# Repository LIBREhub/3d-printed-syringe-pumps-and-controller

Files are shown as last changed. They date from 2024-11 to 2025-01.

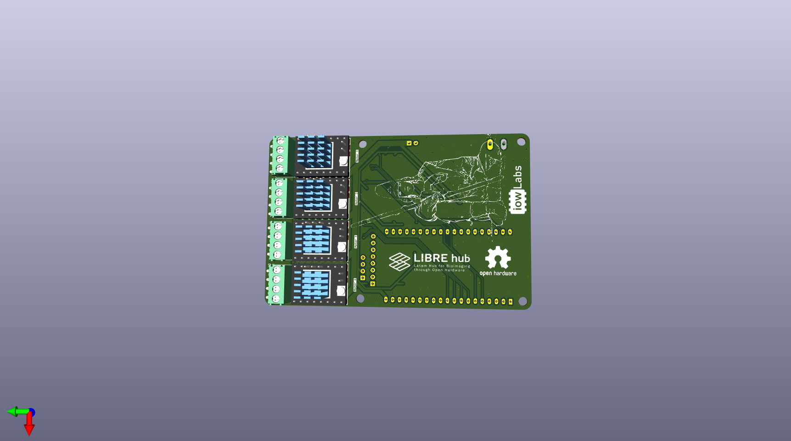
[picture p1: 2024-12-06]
electronics/syringe_pump_controller_module/_versions/ver1/syringe_pump_bottom.png

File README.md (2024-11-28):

# 3D printable syringe pumps and controller  

This project is a free and open-source design of versatile lab equipment - syringe pumps and a dual controller, here detailed for microfluidic droplet generation - a modification from this [Open-Source Syringe Pump design](https://doi.org/10.1134/S1061934820030156).

Find about more about this platform and other open-source hardware for bioimaging on the [LIBRE hub website](https://librehub.github.io/). Follow us! [#twitter](https://twitter.com/WenzelLab) [#YouTube](https://www.youtube.com/@librehub) [#LinkedIn](https://www.linkedin.com/company/92802424) [#instagram](https://www.instagram.com/wenzellab/) [#Printables](https://www.printables.com/@WenzelLab), [IIBM website](https://ingenieriabiologicaymedica.uc.cl/en/people/faculty/821-tobias-wenzel)

## Background

A syringe pump is a device that delivers precise and accurate amounts of fluid over a broad range of flow rates. These devices are versatile and can be used across various fields like healthcare, research, and development, playing a crucial role in scenarios such as controlled drug delivery in hospitals, chemical reaction control in labs, and more.

There are many 3D-printable syringe pump designs available, each with its unique features and capabilities. However, this [Open-Source Syringe Pump design](https://doi.org/10.1134/S1061934820030156) developed by the [Mass Spectrometry Research Group](https://www.mass-spec.ru/projects/diy/syringe_pump/eng/), Analytical Chemistry Division, Chemistry Department of Moscow State University, appealed to our LIBRE Hub team with its design and functionality.

Our goal with this modification and enhancement is to make this open-source syringe pump design more useful to microfluidics and generally more accessible, adaptable, and user-friendly, thus extending its potential use within the broader community.

## Usage

### Instructions
This Repository provides documentation on how to build the pumps and the controller. Just [follow the instructions here](https://wenzel-lab.github.io/syringe-pumps-and-controller/)

This project is documented with GitBuilding - an Open Source project for documenting hardware projects. For more information on the GitBuilding project or how
to install GitBuilding, please see the [GitBuilding website](http://gitbuilding.io)

## Design files and source code

* Hardware design
    * [Link to OnShape CAD files of printable syringe pump parts](https://cad.onshape.com/documents/20c077b452e92115525d4fed/w/71118f46b0924c1bb22b1150/e/9d30ca00efa721d242d78d3f?renderMode=0&uiState=64bd5f2a8bef574246b008b9)
    * [Link to OnShape CAD files of the printable controller enclosure](https://cad.onshape.com/documents/24a5022fafc4edd0c24874dd/w/35c6569cda7c2fa4439727d4/e/9dbcdcaba091e21e6a91c62c?renderMode=0&uiState=64bd5f3f0aa451311c1bb6ad)
* Software source code
    * [Code to upload onto the Raspberry Pi Pico controller](https://github.com/wenzel-lab/syringe-pumps-and-controller/blob/docu-v1/software/firmwareV1.ino)

### How do I edit the documentation?

To edit the documentation, you do not need to install anything, but you will need to
install something to build the final version of the documentation (such as a website).
The documentation files can be opened in a plain text editor such as Windows Notepad,
Notepad++, gedit, VS Code, etc. GitBuilding also comes with a browser-based editor that
displays a live display of the final HTML documentation.

If you have ever used [markdown](https://www.markdownguide.org/basic-syntax/), you will
notice that the files you are editing are markdown files. GitBuilding uses an extended
markdown syntax (that we call BuildUp). This allows you to keep track of parts in the
documentation. More detail on the documentation is available on the
[GitBuilding website](https://gitbuilding.io/syntax/). There is also additional
[syntax for configuration](https://gitbuilding.io/syntax/buildconfsyntax) and for
[part libraries](https://gitbuilding.io/syntax/builduplibrary/).

## Contribute

Enjoy building and using your improved Open-Source Syringe Pump! We look forward to hearing about your experiences and any further improvements you might have. Make a pull request or [open an issue](https://github.com/wenzel-lab/syringe-pumps-and-controller/issues/new).
For interactions in our team and with the community, apply the [GOSH Code of Conduct](https://openhardware.science/gosh-2017/gosh-code-of-conduct/).

## License

[GNU General Public License v3.0](LICENSE) by Tomás Astudillo, Matías Hurtado, Pierre Padilla-Huamantinco, Tobias Wenzel, and the [original design team](https://www.mass-spec.ru/projects/diy/syringe_pump/eng/). This project is Open Source Hardware - please acknowledge us when using the hardware or sharing modifications.

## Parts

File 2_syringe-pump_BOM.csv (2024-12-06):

Name in documentation | Category | Qty | Full Name | Notes
Back support - A | printedparts | 1
Back support - B | printedparts | 1
Carriage | printedparts | 1
Front support | printedparts | 1
Hand knob | printedparts | 2
Heat insert | mech | 6 | Heat inserts
Lead screw | mech | 1 | Threaded Rod
Lead screw nut | mech | 1 | Lead Screw Nut
Linear bearing | mech | 2 | Linear Bearing
Linear motion rods | mech | 2 | Linear Motion Rods
M2.5 hex key | tool | 1
M3 10mm screw | mech | 2 | Screw
M3 12mm screw | mech | 2 | Screw
M3 16mm screw | mech | 8 | Screw
M3 20mm screw | mech | 2 | Screw
M3 8mm screw | mech | 4 | Screw
M3 hex key | tool | 1
M3 nut | mech | 9
M4 10mm screw | mech | 4 | Screw
M4 hex key | tool | 1
Motor coupling | mech | 1 | Motor Coupling
NEMA 17 motor | elect | 1 | Stepper Motor Nema 17
Planetary gearbox 100:1 | mech | 1 | Planetary Gearbox
Soldering iron | tool | 1
Syringe holder | printedparts | 1

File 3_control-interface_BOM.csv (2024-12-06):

Name in documentation | Category | Qty | Full Name | Notes
10 cm female-female jumper | elect | 7
10 cm male-female jumper | elect | 8
20 cm female-female jumper | elect | 12
40 pin header | elect | 1
5.5mm female jack connector | elect | 1
Back cover | printedparts | 1
Electronics holder | printedparts | 1
Interface base | printedparts | 1
Interface panel | printedparts | 1
LCD adapter | printedparts | 1
LCD screen | elect | 1 | LCD Screen
M3 10mm screw | mech | 8 | Screw
M3 16mm screw | mech | 4 | Screw
M3 25mm screw | mech | 1 | Screw
M3 nut | mech | 14
Membrane 4x4 keypad | elect | 1
Raspberry Pi Pico | elect | 1
TMC2209 driver | elect | 2 | Silent Driver + Heatsink
Voltage regulator | elect | 1

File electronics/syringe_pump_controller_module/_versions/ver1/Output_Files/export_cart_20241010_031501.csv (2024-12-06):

LCSC Part Number | Manufacture Part Number | Manufacturer | Package | Customer # | Description | RoHS | Order Qty. | Min\Mult Order Qty. | Unit Price($) | Ext.Price($) | Product Link
C14663 | CC0603KRX7R9BB104 | YAGEO | 0603 |  | 50V 100nF X7R ±10% 0603 Multilayer Ceramic Capacitors MLCC - SMD/SMT ROHS | yes | 100 | 100 | 0.0020 | 0.20 | https://www.lcsc.com/product-detail/multilayer-ceramic-capacitors-mlcc-smd-smt_yageo-cc0603krx7r9bb104_C14663.html
C28323 | CL21B105KBFNNNE | Samsung Electro-Mechanics | 0805 |  | 50V 1uF X7R ±10% 0805 Multilayer Ceramic Capacitors MLCC - SMD/SMT ROHS | yes | 50 | 50 | 0.0088 | 0.44 | https://www.lcsc.com/product-detail/multilayer-ceramic-capacitors-mlcc-smd-smt_samsung-electro-mechanics-cl21b105kbfnnne_C28323.html
C5162345 | CS1E221M-CRF10 | ROQANG | SMD,D8xL10.5mm |  | 220uF 25V 183mA@120Hz ±20% SMD,D8xL10.5mm Aluminum Electrolytic Capacitors - SMD ROHS | yes | 10 | 10 | 0.0604 | 0.60 | https://www.lcsc.com/product-detail/aluminum-electrolytic-capacitors-smd_roqang-cs1e221m-crf10_C5162345.html
C5162349 | CS1E331M-CRF10 | ROQANG | SMD,D8xL10.5mm |  | 330uF 25V 228mA@120Hz ±20% SMD,D8xL10.5mm Aluminum Electrolytic Capacitors - SMD ROHS | yes | 10 | 10 | 0.0444 | 0.44 | https://www.lcsc.com/product-detail/aluminum-electrolytic-capacitors-smd_roqang-cs1e331m-crf10_C5162349.html
C3019736 | ACDBB540-HF | Comchip | SMB |  | 40V Independent Type 550mV@5A 5A SMB Schottky Diodes ROHS | yes | 5 | 5 | 0.2341 | 1.17 | https://www.lcsc.com/product-detail/schottky-diodes_comchip-acdbb540-hf_C3019736.html
C12624 | KT-0603G | Hubei KENTO Elec | 0603 |  | Emerald 0603 LED Indication - Discrete ROHS | yes | 50 | 50 | 0.0104 | 0.52 | https://www.lcsc.com/product-detail/led-indication-discrete_hubei-kento-elec-kt-0603g_C12624.html
C553921 | S1206-F-1.0A | SART(Nanjing Sart Tech) | 1206 |  | 50A SMD Fuse 1A 32V 1206 Disposable fuses ROHS | yes | 10 | 10 | 0.0686 | 0.69 | https://www.lcsc.com/product-detail/disposable-fuses_sart-nanjing-sart-tech-s1206-f-1-0a_C553921.html
C2840319 | TY500-5.0-02P-14-00AH | Toponelec | Plugin,P=5mm |  | 1x2P 20A -40℃~+105℃ 300V Green 12~30 Direct Insert 5mm 1~2.5 1 2 Plugin,P=5mm Screw Terminal Blocks ROHS | yes | 5 | 1 | 0.1999 | 1.00 | https://www.lcsc.com/product-detail/screw-terminal-blocks_toponelec-ty500-5-0-02p-14-00ah_C2840319.html
C557656 | XY350V-3.5-4P | Ningbo Xinlaiya Elec. | Plugin,P=3.5mm |  | Copper 1x4P Tin 3.5mm 1 1 4 7A 300V Green 18~24 Direct Insert Plugin,P=3.5mm Screw Terminal Blocks ROHS | yes | 20 | 5 | 0.2307 | 4.61 | https://www.lcsc.com/product-detail/screw-terminal-blocks_ningbo-xinlaiya-elec-xy350v-3-5-4p_C557656.html
C8677 | XH-2Y | BOOMELE(Boom Precision Elec) | P=2.5mm |  | 2.5mm 1x2P XH 2 1 P=2.5mm Housings (Wire To Board / Wire To Wire ) ROHS | yes | 100 | 100 | 0.0035 | 0.35 | https://www.lcsc.com/product-detail/housings-wire-to-board-wire-to-wire_boomele-boom-precision-elec-xh-2y_C8677.html
C20079 | XH-2A | BOOMELE(Boom Precision Elec) | Plugin,P=2.5mm |  | 1x2P 2P XH 1 2.5mm 2 Plugin,P=2.5mm Wire To Board Connector ROHS | yes | 100 | 100 | 0.0067 | 0.67 | https://www.lcsc.com/product-detail/wire-to-board-connector_boomele-boom-precision-elec-xh-2a_C20079.html
C5116530 | PM2.54-1*4 | ZHOURI | Plugin,P=2.54mm |  | 2.54mm 2.54mm Single Row 2.5A 4P -40℃~+105℃ Direct Insert 1x4P Top 8.5mm Square Hole Plugin,P=2.54mm Female Headers ROHS | yes | 5 | 5 | 0.0711 | 0.36 | https://www.lcsc.com/product-detail/female-headers_zhouri-pm2-54-1-4_C5116530.html
C5224027 | PM2.54-1*8 | ZHOURI | Plugin,P=2.54mm |  | 2.54mm 2.54mm Single Row 2.5A 8P -40℃~+105℃ Direct Insert 1x8P Top 8.5mm Square Hole Plugin,P=2.54mm Female Headers ROHS | yes | 5 | 5 | 0.0916 | 0.46 | https://www.lcsc.com/product-detail/female-headers_zhouri-pm2-54-1-8_C5224027.html
C2929502 | CYH127-33UH | SHOU HAN | SMD,12.3x12.3mm |  | 3A 33uH ±20% 64.8mΩ SMD,12.3x12.3mm Inductors (SMD) ROHS | yes | 5 | 5 | 0.2669 | 1.33 | https://www.lcsc.com/product-detail/inductors-smd_shou-han-cyh127-33uh_C2929502.html
C98220 | RC0603FR-0710KL | YAGEO | 0603 |  | 100mW Thick Film Resistors 75V ±100ppm/℃ ±1% 10kΩ 0603 Chip Resistor - Surface Mount ROHS | yes | 200 | 100 | 0.0010 | 0.20 | https://www.lcsc.com/product-detail/chip-resistor-surface-mount_yageo-rc0603fr-0710kl_C98220.html
C22548 | RC0603FR-071KL | YAGEO | 0603 |  | 100mW Thick Film Resistors 75V ±100ppm/℃ ±1% 1kΩ 0603 Chip Resistor - Surface Mount ROHS | yes | 100 | 100 | 0.0010 | 0.10 | https://www.lcsc.com/product-detail/chip-resistor-surface-mount_yageo-rc0603fr-071kl_C22548.html
C25995 | 0603WAJ0332T5E | UNI-ROYAL(Uniroyal Elec) | 0603 |  | 100mW Thick Film Resistors 75V ±100ppm/℃ ±5% 3.3kΩ 0603 Chip Resistor - Surface Mount ROHS | yes | 100 | 100 | 0.0009 | 0.09 | https://www.lcsc.com/product-detail/chip-resistor-surface-mount_uni-royal-uniroyal-elec-0603waj0332t5e_C25995.html
C51118 | AP2112K-3.3TRG1 | Diodes Incorporated | SOT-25-5 |  | 65dB@(100Hz,1kHz) 600mA Fixed 3.3V Positive electrode 6V SOT-25-5 Voltage Regulators - Linear, Low Drop Out (LDO) Regulators ROHS | yes | 5 | 5 | 0.0692 | 0.35 | https://www.lcsc.com/product-detail/voltage-regulators-linear-low-drop-out-ldo-regulators_diodes-incorporated-ap2112k-3-3trg1_C51118.html
C51661 | XL4015E1 | XLSEMI | TO-263-5 |  | Step-down type 5A 8V~36V TO-263-5 DC-DC Converters ROHS | yes | 5 | 1 | 0.5826 | 2.91 | https://www.lcsc.com/product-detail/dc-dc-converters_xlsemi-xl4015e1_C51661.html
C22396383 | PCF8574DWR(UMW) | UMW(Youtai Semiconductor Co., Ltd.) | SOIC-16-300mil |  | SOIC-16-300mil I/O Expanders ROHS | yes | 5 | 1 | 0.4569 | 2.28 | https://www.lcsc.com/product-detail/i-o-expanders_umw-youtai-semiconductor-co-ltd-pcf8574dwr-umw_C22396383.html
C128392 | PCA9555PW,118 | NXP Semicon | TSSOP-24 |  | 16 400kHz TSSOP-24 I/O Expanders ROHS | yes | 5 | 1 | 0.8596 | 4.30 | https://www.lcsc.com/product-detail/i-o-expanders_nxp-semicon-pca9555pw-118_C128392.html
C529577 | ESP32-WROOM-32D-N8 | Espressif Systems | SMD,18x25.5mm |  | SMD,18x25.5mm WiFi Modules ROHS | yes | 5 | 1 | 4.0019 | 20.01 | https://www.lcsc.com/product-detail/wifi-modules_espressif-systems-esp32-wroom-32d-n8_C529577.html

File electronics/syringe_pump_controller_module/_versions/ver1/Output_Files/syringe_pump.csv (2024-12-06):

Reference | Value | Datasheet | Footprint | Qty | DNP
C1,C3,C4,C5,C6,C19,C20,C21,C22 | 1u |  | Capacitor_SMD:C_0805_2012Metric | 9
C2 | 220uF | ~ | Capacitor_SMD:CP_Elec_8x10.5 | 1
C7 | 330uF | ~ | Capacitor_SMD:CP_Elec_8x10.5 | 1
C13,C14,C15,C16,C17,C18 | 100n |  | Capacitor_SMD:C_0603_1608Metric | 6
D1,D3,D4 | LED | ~ | LED_SMD:LED_0603_1608Metric | 3
D2 | B540 | ~ | Diode_SMD:D_SMB_Handsoldering | 1
F2 | FUSE |  | Fuse:Fuse_1206_3216Metric | 1
J1 | IN |  | IoWLabsConnectors:Tb-2x1-5p-TH-V | 1
J2 | ON OFF |  | Connector_PinHeader_2.54mm:PinHeader_1x02_P2.54mm_Vertical | 1
J4,J5,J8,J9 | HDR-4x1 |  | TerminalBlock_Phoenix:TerminalBlock_Phoenix_PT-1,5-4-3.5-H_1x04_P3.50mm_Horizontal | 4
J6,J7,J10,J11 | EndSwitch |  | IoWLabsConnectors:JST-XH-2x1-2.5p-TH-V | 4
J12 | Conn_01x04 | ~ | Connector_PinSocket_2.54mm:PinSocket_1x04_P2.54mm_Vertical | 1
J13 | Conn_01x08 | ~ | Connector_PinSocket_2.54mm:PinSocket_1x08_P2.54mm_Vertical | 1
L1 | 47uH | ~ | Inductor_SMD:L_12x12mm_H8mm | 1
R1,R2,R3,R19,R20,R23,R24 | 1k |  | Resistor_SMD:R_0603_1608Metric | 7
R4,R13,R14,R15,R16,R17,R18 | 10K |  | Resistor_SMD:R_0603_1608Metric | 7
R5 | 3.3K |  | Resistor_SMD:R_0603_1608Metric | 1
R7,R8,R21,R22,R25,R26,R27,R28,R29,R30,R31 | 10k |  | Resistor_SMD:R_0603_1608Metric | 11
U1 | AP2112K-3.3 | https://www.diodes.com/assets/Datasheets/AP2112.pdf | Package_TO_SOT_SMD:SOT-23-5 | 1
U2 | XL4015 | http://www.xlsemi.net/datasheet/XL4015%20datasheet-English.pdf | Package_TO_SOT_SMD:TO-263-5_TabPin3 | 1
U5 | MCP23017_SO | http://ww1.microchip.com/downloads/en/DeviceDoc/20001952C.pdf | Package_SO:SOIC-28W_7.5x17.9mm_P1.27mm | 1
U6 | PCF8574 | http://www.nxp.com/docs/en/data-sheet/PCF8574_PCF8574A.pdf | Package_SO:SOIC-16W_7.5x10.3mm_P1.27mm | 1
U7 | ESP32-DevKitC | https://docs.espressif.com/projects/esp-idf/zh_CN/latest/esp32/hw-reference/esp32/get-started-devkitc.html | Espressif:ESP32-DevKitC | 1
X1,X2,X3,X4 | ~ |  | IoWLabsModules:TCM2209 | 4

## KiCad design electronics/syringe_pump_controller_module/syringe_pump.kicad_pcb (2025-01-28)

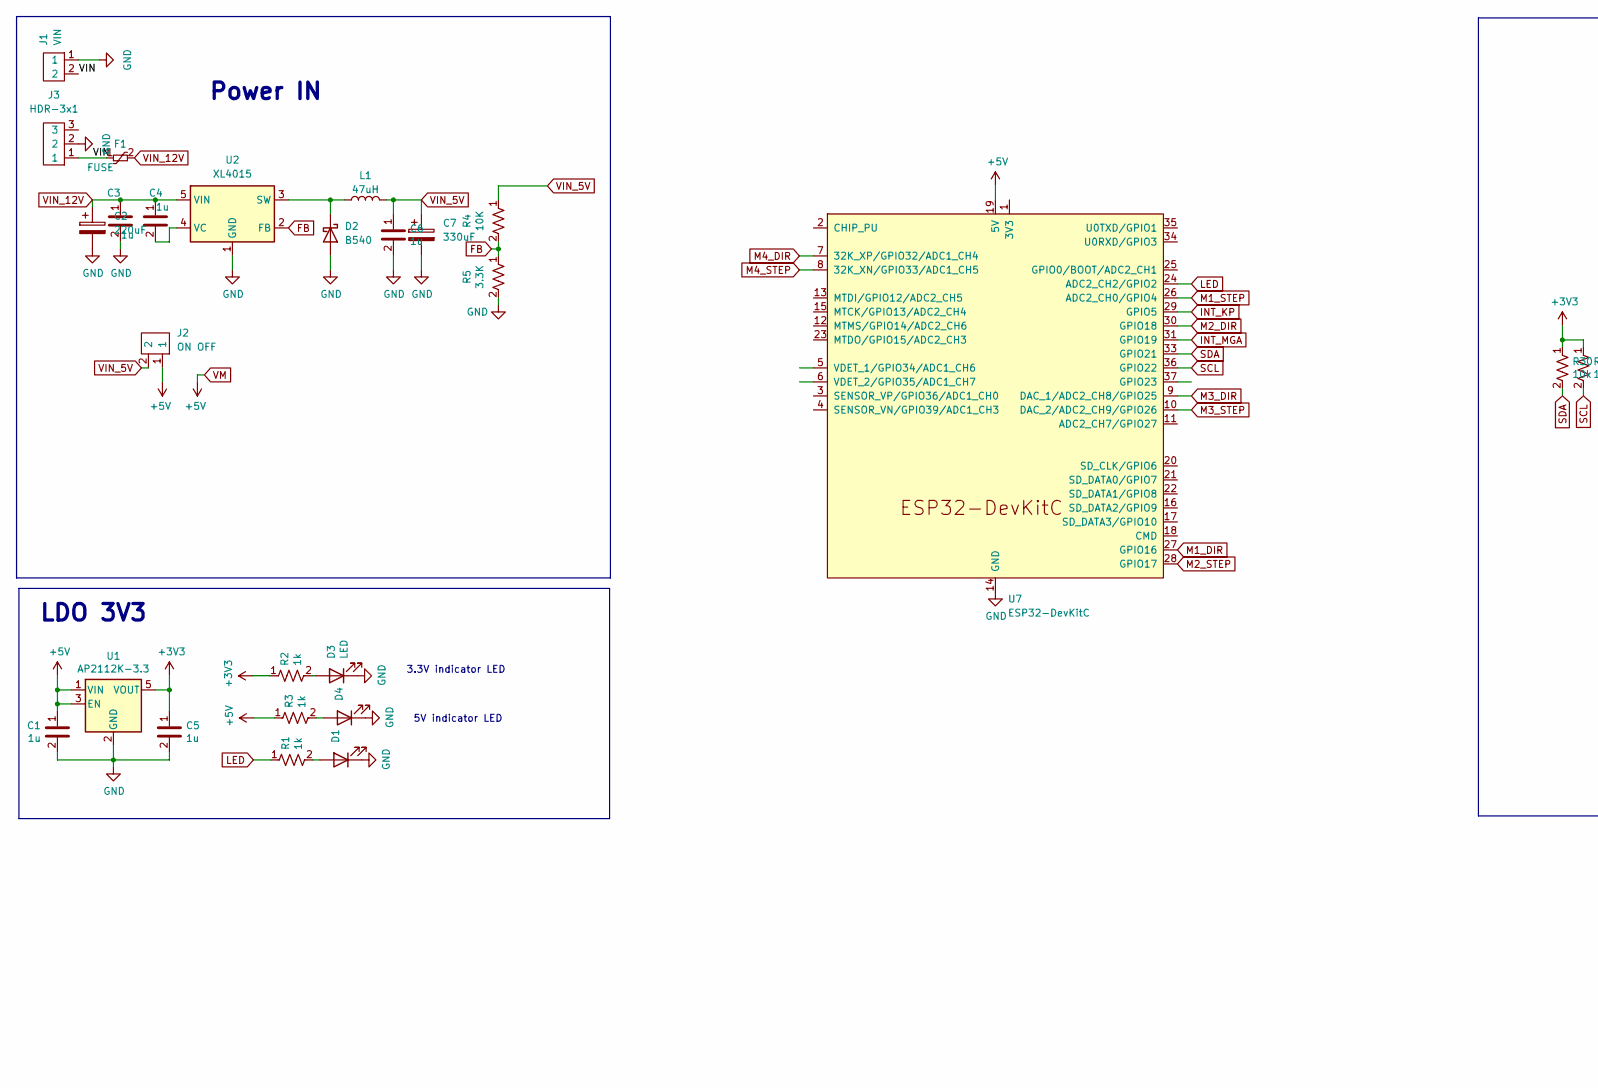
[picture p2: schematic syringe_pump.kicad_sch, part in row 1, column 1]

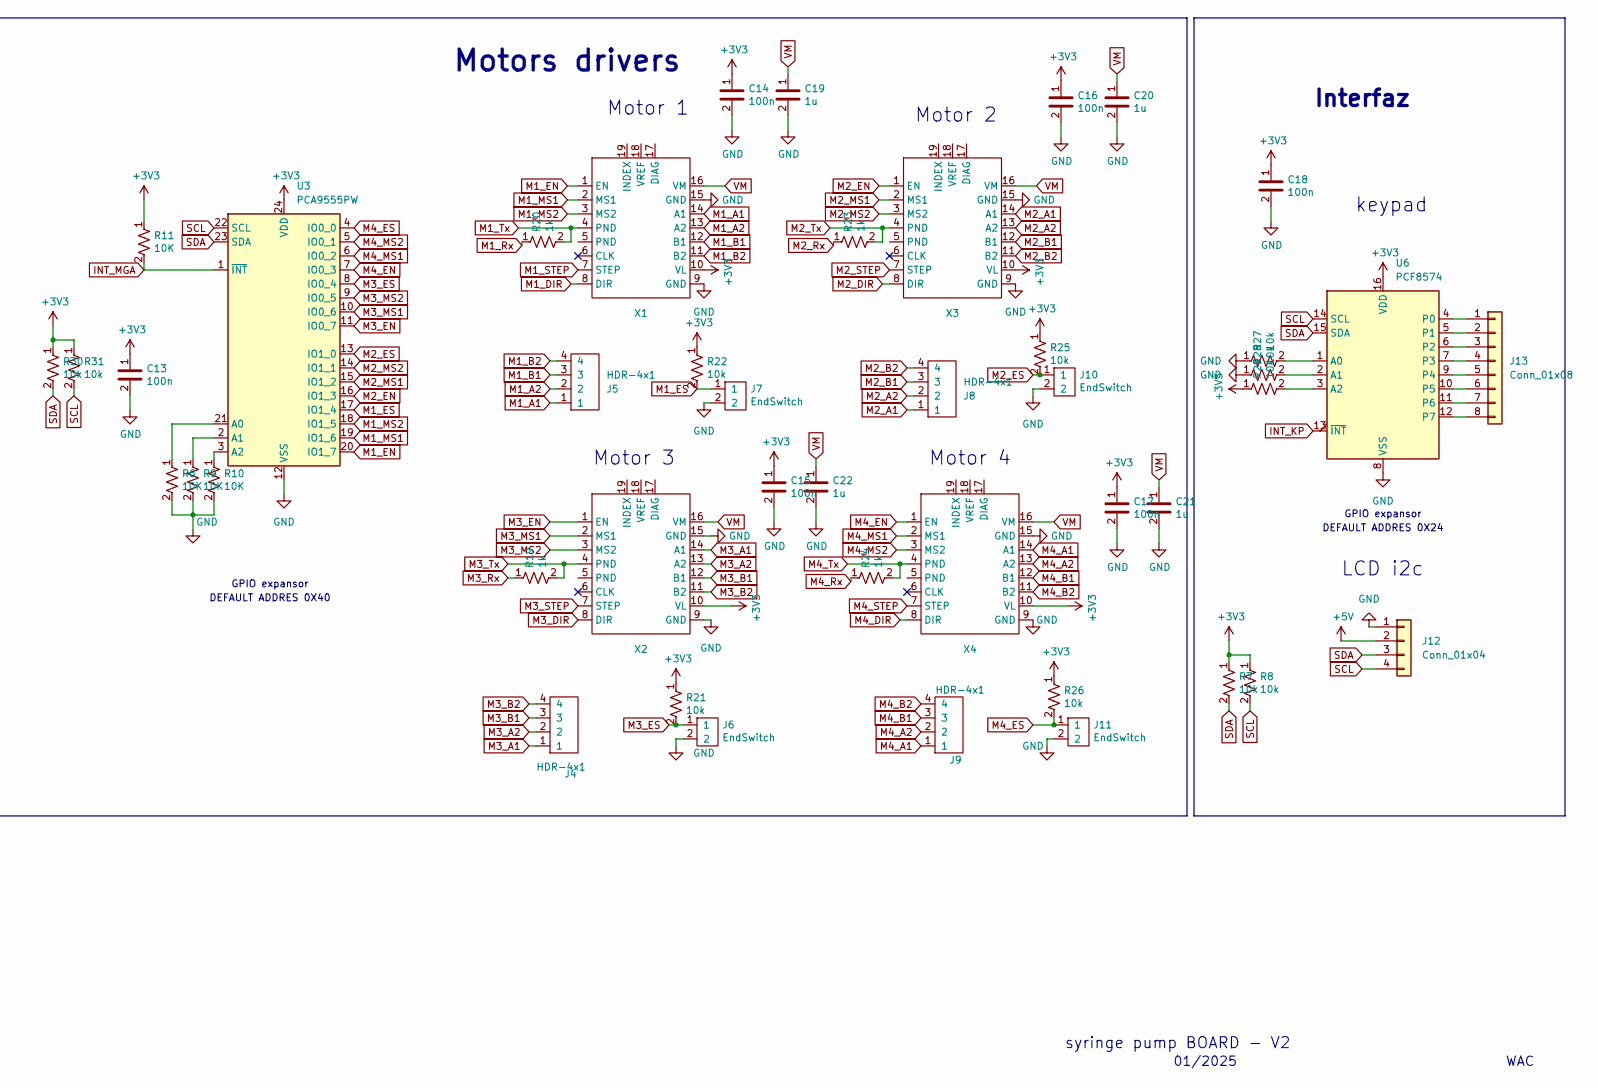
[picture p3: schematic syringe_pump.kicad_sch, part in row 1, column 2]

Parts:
C1, C3, C4, C5, C6, C19, C20, C21, C22: 1u; C_0805_2012Metric; Voltage rated 16V
C2: 220uF; CP_Elec_8x10.5; Voltage 50V
C7: 330uF; CP_Elec_8x10.5; Voltage 25V
C13, C14, C15, C16, C17, C18: 100n; C_0603_1608Metric; Voltage rated 16V
D1, D3, D4: LED; LED_0603_1608Metric
D2: B540; D_SMB_Handsoldering
F1: FUSE; Fuse_1206_3216Metric
J1: VIN; Tb-2x1-5p-TH-V
J2: ON OFF; PinHeader_1x02_P2.54mm_Vertical
J3: HDR-3x1; BarrelJack_Horizontal
J4, J5, J8, J9: HDR-4x1; TerminalBlock_Phoenix_PT-1,5-4-3.5-H_1x04_P3.50mm_Horizontal
J6, J7, J10, J11: EndSwitch; JST-XH-2x1-2.5p-TH-V
J12: Conn_01x04; PinSocket_1x04_P2.54mm_Vertical
J13: Conn_01x08; PinSocket_1x08_P2.54mm_Vertical
L1: 47uH; L_12x12mm_H8mm
R1, R2, R3, R19, R20, R23, R24: 1k; R_0603_1608Metric
R4, R6, R9, R10, R11: 10K; R_0603_1608Metric
R5: 3.3K; R_0603_1608Metric
R7, R8, R21, R22, R25, R26, R27, R28, R29, R30, R31: 10k; R_0603_1608Metric
U1: AP2112K-3.3; SOT-23-5
U2: XL4015; TO-263-5_TabPin3
U3: PCA9555PW; TSSOP-24_4.4x7.8mm_P0.65mm
U6: PCF8574; SOIC-16W_7.5x10.3mm_P1.27mm
U7: ESP32-DevKitC
X1, X2, X3, X4: TCM2209

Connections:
+3V3: C5.1, C13.1, C14.1, C15.1, C16.1, C17.1, C18.1, R2.1, R7.1, R8.1, R11.1, R21.1, R22.1, R25.1, R26.1, R29.1, R30.1, R31.1, U1.5 (VOUT), U3.24 (VDD), U6.16 (VDD), X1.10 (VL), X2.10 (VL), X3.10 (VL), X4.10 (VL)
/VIN: F1.1, J1.2, J3.1
FB: R4.2, R5.1, U2.2 (FB)
GND: C1.2, C2.2, C3.2, C5.2, C6.2, C7.2, C13.2, C14.2, C15.2, C16.2, C17.2, C18.2, C19.2, C20.2, C21.2, C22.2, D1.1 (K), D2.2 (A), D3.1 (K), D4.1 (K), J1.1, J3.2, J6.2, J7.2, J10.2, J11.2, J12.1, R5.2, R6.2, R9.2, R10.2, R27.1, R28.1, U1.2 (GND), U2.1 (GND), U3.12 (VSS), U6.8 (VSS), U7.14 (GND), U7.32 (GND), U7.38 (GND), X1.9 (GND), X1.15 (GND), X2.9 (GND), X2.15 (GND), X3.9 (GND), X3.15 (GND), X4.9 (GND), X4.15 (GND)
INT_KP: U6.13 (~INT), U7.29 (GPIO5)
INT_MGA: R11.2, U3.1 (~INT), U7.31 (GPIO19)
LED: R1.1, U7.24 (ADC2_CH2/GPIO2)
M1_A1: J5.1, X1.14 (A1)
M1_A2: J5.2, X1.13 (A2)
M1_B1: J5.3, X1.12 (B1)
M1_B2: J5.4, X1.11 (B2)
M1_DIR: U7.27 (GPIO16), X1.8 (DIR)
M1_EN: U3.20 (IO1_7), X1.1 (EN)
M1_ES: J7.1, R22.2, U3.17 (IO1_4)
M1_MS1: U3.19 (IO1_6), X1.2 (MS1)
M1_MS2: U3.18 (IO1_5), X1.3 (MS2)
M1_STEP: U7.26 (ADC2_CH0/GPIO4), X1.7 (STEP)
M1_Tx: R20.2, X1.4 (PND)
M2_A1: J8.1, X3.14 (A1)
M2_A2: J8.2, X3.13 (A2)
M2_B1: J8.3, X3.12 (B1)
M2_B2: J8.4, X3.11 (B2)
M2_DIR: U7.30 (GPIO18), X3.8 (DIR)
M2_EN: U3.16 (IO1_3), X3.1 (EN)
M2_ES: J10.1, R25.2, U3.13 (IO1_0)
M2_MS1: U3.15 (IO1_2), X3.2 (MS1)
M2_MS2: U3.14 (IO1_1), X3.3 (MS2)
M2_STEP: U7.28 (GPIO17), X3.7 (STEP)
M2_Tx: R23.2, X3.4 (PND)
M3_A1: J4.1, X2.14 (A1)
M3_A2: J4.2, X2.13 (A2)
M3_B1: J4.3, X2.12 (B1)
M3_B2: J4.4, X2.11 (B2)
M3_DIR: U7.9 (DAC_1/ADC2_CH8/GPIO25), X2.8 (DIR)
M3_EN: U3.11 (IO0_7), X2.1 (EN)
M3_ES: J6.1, R21.2, U3.8 (IO0_4)
M3_MS1: U3.10 (IO0_6), X2.2 (MS1)
M3_MS2: U3.9 (IO0_5), X2.3 (MS2)
M3_STEP: U7.10 (DAC_2/ADC2_CH9/GPIO26), X2.7 (STEP)
M3_Tx: R19.2, X2.4 (PND)
M4_A1: J9.1, X4.14 (A1)
M4_A2: J9.2, X4.13 (A2)
M4_B1: J9.3, X4.12 (B1)
M4_B2: J9.4, X4.11 (B2)
M4_DIR: U7.7 (32K_XP/GPIO32/ADC1_CH4), X4.8 (DIR)
M4_EN: U3.7 (IO0_3), X4.1 (EN)
M4_ES: J11.1, R26.2, U3.4 (IO0_0)
M4_MS1: U3.6 (IO0_2), X4.2 (MS1)
M4_MS2: U3.5 (IO0_1), X4.3 (MS2)
M4_STEP: U7.8 (32K_XN/GPIO33/ADC1_CH5), X4.7 (STEP)
M4_Tx: R24.2, X4.4 (PND)
unnamed: D1.2 (A), R1.2
unnamed: D2.1 (K), L1.1, U2.3 (SW)
unnamed: D3.2 (A), R2.2
unnamed: D4.2 (A), R3.2
unnamed: J13.1, U6.4 (P0)
unnamed: J13.2, U6.5 (P1)
unnamed: J13.3, U6.6 (P2)
unnamed: J13.4, U6.7 (P3)
unnamed: J13.5, U6.9 (P4)
unnamed: J13.6, U6.10 (P5)
unnamed: J13.7, U6.11 (P6)
unnamed: J13.8, U6.12 (P7)
unnamed: C4.2, U2.4 (VC)
unnamed: R6.1, U3.21 (A0)
unnamed: R9.1, U3.2 (A1)
unnamed: R10.1, U3.3 (A2)
unnamed: R27.2, U6.1 (A0)
unnamed: R28.2, U6.2 (A1)
unnamed: R29.2, U6.3 (A2)
SCL: J12.4, R8.2, R31.2, U3.22 (SCL), U6.14 (SCL), U7.36 (GPIO22)
SDA: J12.3, R7.2, R30.2, U3.23 (SDA), U6.15 (SDA), U7.33 (GPIO21)
VIN_5V: C6.1, C7.1, J2.2, L1.2, R4.1
VIN_12V: C2.1, C3.1, C4.1, F1.2, U2.5 (VIN)
VM: C1.1, C19.1, C20.1, C21.1, C22.1, J2.1, J12.2, R3.1, U1.1 (VIN), U1.3 (EN), U7.19 (5V), X1.16 (VM), X2.16 (VM), X3.16 (VM), X4.16 (VM)

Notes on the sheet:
Motor 2
Motors drivers
Interfaz
3.3V indicator LED
keypad
GPIO expansor
WAC
DEFAULT ADDRES 0X40
syringe pump BOARD - V2
LCD i2c
01/2025
Motor 3
Power IN
Motor 1
DEFAULT ADDRES 0X24
5V indicator LED
Motor 4
LDO 3V3

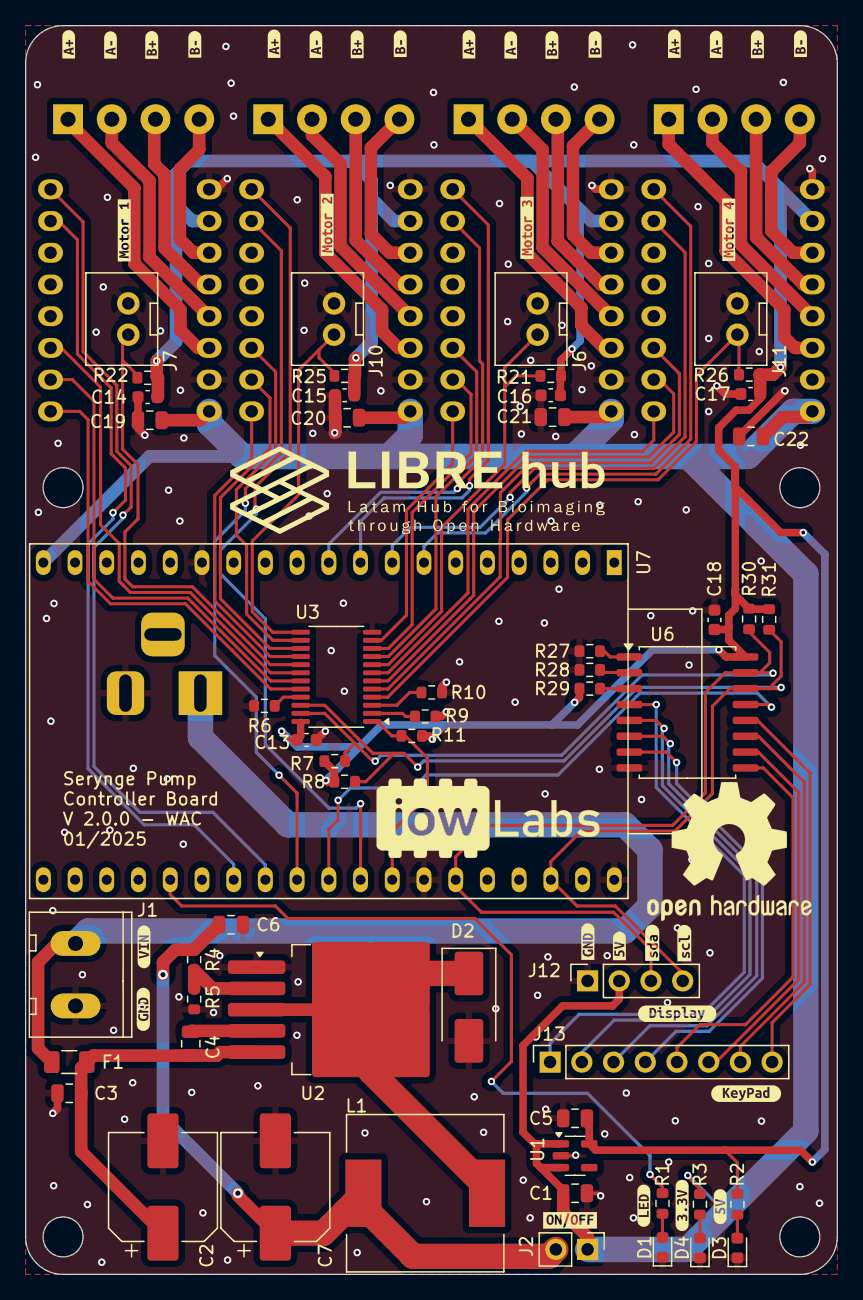
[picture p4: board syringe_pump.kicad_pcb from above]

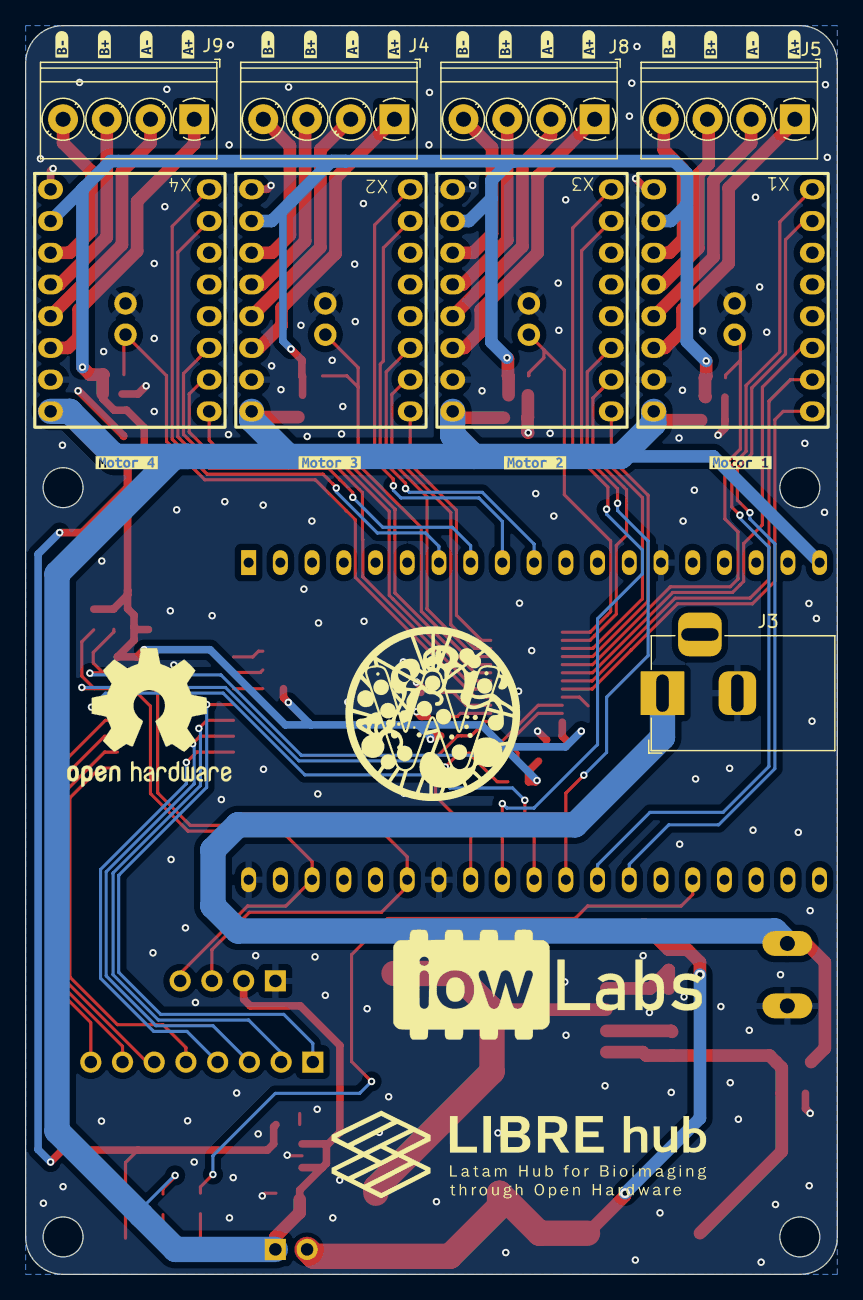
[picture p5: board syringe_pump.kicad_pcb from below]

Board: 2 copper layers, 65.0 x 100.0 mm, 117 parts (29 on the bottom side), 71 nets.

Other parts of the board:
kibuzzard-66A405FA: G***; kibuzzard-66A405FA
kibuzzard-66A40617: G***; kibuzzard-66A40617
kibuzzard-66C22E4F, kibuzzard-66C22E4F#2, kibuzzard-66C22E4F#3, kibuzzard-66C22E4F#4, kibuzzard-66C22E4F#5, kibuzzard-66C22E4F#6, kibuzzard-66C22E4F#7, kibuzzard-66C22E4F#8: G***; kibuzzard-66C22E4F
kibuzzard-66C22E62, kibuzzard-66C22E62#2, kibuzzard-66C22E62#3, kibuzzard-66C22E62#4, kibuzzard-66C22E62#5, kibuzzard-66C22E62#6, kibuzzard-66C22E62#7, kibuzzard-66C22E62#8: G***; kibuzzard-66C22E62
kibuzzard-66C22E71, kibuzzard-66C22E71#2, kibuzzard-66C22E71#3, kibuzzard-66C22E71#4, kibuzzard-66C22E71#5, kibuzzard-66C22E71#6, kibuzzard-66C22E71#7, kibuzzard-66C22E71#8: G***; kibuzzard-66C22E71
kibuzzard-66C22E91, kibuzzard-66C22E91#2, kibuzzard-66C22E91#3, kibuzzard-66C22E91#4, kibuzzard-66C22E91#5, kibuzzard-66C22E91#6, kibuzzard-66C22E91#7, kibuzzard-66C22E91#8: G***; kibuzzard-66C22E91
kibuzzard-66C26F7C: G***; kibuzzard-66C26F7C
kibuzzard-66C268D3, kibuzzard-66C268D3#2: G***; kibuzzard-66C268D3
kibuzzard-66C268F5, kibuzzard-66C268F5#2: G***; kibuzzard-66C268F5
kibuzzard-66C271FC: G***; kibuzzard-66C271FC
kibuzzard-66C2695E, kibuzzard-66C2695E#2: G***; kibuzzard-66C2695E
kibuzzard-66C26938, kibuzzard-66C26938#2: G***; kibuzzard-66C26938
kibuzzard-66C27154: G***; kibuzzard-66C27154
kibuzzard-66C27168: G***; kibuzzard-66C27168
kibuzzard-66C27204: G***; kibuzzard-66C27204
kibuzzard-66C27242: G***; kibuzzard-66C27242
kibuzzard-678D37F1: G***; kibuzzard-678D37F1
kibuzzard-678D375F: G***; kibuzzard-678D375F
kibuzzard-678D3724: G***; kibuzzard-678D3724
kibuzzard-678D3737: G***; kibuzzard-678D3737

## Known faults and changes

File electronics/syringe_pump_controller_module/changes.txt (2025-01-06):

V1.0.0
Cosas que corregir:
	- Los pines SDA y SCL estan invertidos en el componente U3 (PCA955P)
	- Los conectores J11 y J12 del display y del key oad deben correrse para no estorbar el usb

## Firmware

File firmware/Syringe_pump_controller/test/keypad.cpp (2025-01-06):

//    FILE: I2CKeypad_interrupts_1.ino
//  AUTHOR: Rob Tillaart
// PURPOSE: demo interrupt checking keyPressed
//     URL: https://github.com/RobTillaart/I2CKeyPad
//
//  interrupts are supported since version 0.2.1
//  this sketch show usage and some comparison with polling.
//
//   KEYPAD   PCF8574     UNO
//   rows     p0-p3
//   columns  p4-p7
//            IRQ         pin 2
//            SDA         A4
//            SCL         A5
//  4x4 or smaller keypad.


//  notes
//  an interrupt takes less than 10 micros() on an UNO
//  source - https://forum.arduino.cc/t/how-fast-can-i-interrupt/25884/6
//
//  At I2C 100KHz one polling takes 472 micros() on an UNO
//  this is at least 50x longer than handling a single interrupt.
//
//  Given that the interrupt is executed once per press/release and
//  polling at e.g 10Hz (to stay reactive) adds up both in CPU time used
//  and also in occupation of the I2C bus.
//
//  The PCF8574 will generate an interrupt both on press and release.
//  So this code reads the keypad on both signals!
//
//  Note: depending on keypad used some bouncing may occur
//        (saw it only during release)
//  can be solved by tracking the last interrupt in the ISR routine
//  however it is more efficient to reset the flag only after the
//  keypress is handled.
//
//  Note: multiple keypresses are not queued.


////////////////////////////////////////////////////////////////////////
//
//

#include <Arduino.h>
#include <Wire.h>
#include <I2CKeyPad.h>
#include <LiquidCrystal_I2C.h>
#include "clsPCA9555.h"
#include "freertos/FreeRTOS.h"
#include "freertos/task.h"
#include "freertos/semphr.h"
#include <WiFi.h>
#include <PubSubClient.h>
#include <ArduinoJson.h>





#define ID "SPC-01"
#define VERSION "SP-v0.1"
#define RESPONSE_OK     		"OK"
#define RESPONSE_ERROR  		"ERROR"
#define RESPONSE_ERROR_JSON  	"ERROR_INPUT_JSON"
#define RESPONSE_ERROR_CMD 		"ERROR_CMD"

//MQTT
#define PUBLISH_TOPIC  	"wl/sp/tx"
#define SUBSCRIBE_TOPIC "wl/sp/rx"

#define mqtt_server 	"35.223.234.244"
#define mqtt_user 		"iowlabs"
#define mqtt_password 	"!iow_woi!"
#define mqtt_port 1883


// Configuración de la red Wi-Fi
const char* ssid = "Taller.1";
const char* password = "@Salvo20";

#define STEP_2_mL 25

// Configuración del cliente Wi-Fi y MQTT
WiFiClient espClient;
PubSubClient client(espClient);

PCA9555 ioport(0x20);
LiquidCrystal_I2C lcd(0x27,16,2);  //

//Task to handel mqtt rcv commands
TaskHandle_t Task1;

//cmd
const char* cmd;
const char* rcvd_id;
const char* response = RESPONSE_OK;

//KEYPAD
const uint8_t KEYPAD_ADDRESS = 0x24;
I2CKeyPad keyPad(KEYPAD_ADDRESS);
char keys[] = "123A456B789C*0#DNF";  //  N = NoKey, F = Fail (e.g. > 1 keys pressed)


// Pines del motor stepper
int EN_PINS[] 	= {15,11,0,4};
int STEP_PINS[] = {18,16,32,25};
int DIR_PINS[]  = {17,4,33,26};

// volatile for IRQ var
volatile bool keyChange = false;
String inputNumber = ""; // Para almacenar el número ingresado
int channel = 2;
int steps = 0;
bool bussy_mqtt = false;

void moveStepper(int _steps, int _ch);
void keyChanged();
void setup_wifi();
void reconnect();
void processCmd(byte* payload, unsigned int length);
void publishMqtt(char *payload);
void publishResponse();
void callback(char* topic, byte* payload, unsigned int length);
void measurePolling();
void Task1code(void *pvParameters);

void setup()
{
	Serial.begin(115200);

	setup_wifi();
	client.setServer(mqtt_server, mqtt_port);
	client.setCallback(callback);

  	//  NOTE: PCF8574 will generate an interrupt on key press and release.
  	pinMode(5, INPUT_PULLUP);
  	attachInterrupt(5, keyChanged, FALLING);
  	keyChange = false;

	Wire.begin();

	Wire.setClock(100000);
	if (keyPad.begin() == false)
	{
		Serial.println("\nERROR: cannot communicate to keypad.\nPlease reboot.\n");
	}

	ioport.begin();

	//Define pin modes
	for(int i = 0;i<4;i++)
	{
		ioport.pinMode(EN_PINS[i], OUTPUT);
		ioport.digitalWrite(EN_PINS[i], HIGH);

		pinMode(DIR_PINS[i],OUTPUT);
		pinMode(STEP_PINS[i],OUTPUT);
	}


	lcd.init();
	lcd.backlight();
	// Escribimos el Mensaje en el LCD.
	lcd.setCursor(0, 0);
	lcd.print("SP - ctrl");

	delay(100);
	// Task 1 for handle mqtt reception
	xTaskCreatePinnedToCore(
                    Task1code,   /* Task function. */
                    "Task1",     /* name of task. */
                    10000,       /* Stack size of task */
                    NULL,        /* parameter of the task */
                    1,           /* priority of the task */
                    &Task1,      /* Task handle to keep track of created task */
                    0);          /* pin task to core 0 */
  	delay(500);

	measurePolling();
}


void loop()
{
	if (keyChange)
	{
    	uint8_t index = keyPad.getKey();
    	keyChange = false; // Reinicia la bandera de interrupción

    	if (index != 16)
		{ // Si se detecta una tecla
      		char key = keys[index];

      		if (key >= '0' && key <= '9')
			{
        		// Concatenar el número ingresado
        		inputNumber += key;
        		lcd.setCursor(0, 1);
        		lcd.print("ml: ");
        		lcd.print(inputNumber);
      		}
			else if (key == 'D')
			{
        		// Ejecutar el movimiento del motor con los pasos ingresados
        		steps = inputNumber.toInt();

				lcd.setCursor(0, 0);
        		Serial.print("Ejecutando ");

				Serial.print(steps);
        		Serial.println(" pasos.");

        		lcd.setCursor(0, 1);
        		lcd.print("Moviendo...      ");
        		moveStepper(steps,channel);

        		// Reiniciar el número ingresado
        		inputNumber = "";
        		lcd.setCursor(0, 1);
        		lcd.print("Listo           ");
      		}
			else if (key == '*')
			{
        		// Limpiar el número ingresado
        		inputNumber = "";
        		lcd.setCursor(0, 1);
        		lcd.print("                "); // Borrar línea
        		lcd.setCursor(0, 0);
        		lcd.print("Ingrese ml:");
      		}
    	}
  	}
}

void Task1code( void * pvParameters )
{
 	Serial.print("Task1 running on core ");
 	Serial.println(xPortGetCoreID());

	for(;;)
	{
		if (bussy_mqtt == false)
		{
			if (!client.connected())
			{
	    		reconnect();
	  		}
		}

		client.loop();

    	vTaskDelay(1);  // Cede el control por un tick del sistema
  	}
}

// Función de callback para manejar mensajes recibidos
void callback(char* topic, byte* payload, unsigned int length)
{
	Serial.print("Mensaje recibido en el tema: ");
	Serial.println(topic);
	Serial.print("Contenido: ");
	for (unsigned int i = 0; i < length; i++)
 	{
		Serial.print((char)payload[i]);
	}
	Serial.println("");
	processCmd(payload,length);
}

void publishMqtt(char *payload)
{
	bussy_mqtt = true;
	Serial.print("sending data by mqtt . . .");
	client.publish(PUBLISH_TOPIC, payload , true);
	Serial.println(" done");
	bussy_mqtt = false;
}

void setup_wifi()
{
	delay(10);
	Serial.println("Conectando a Wi-Fi...");
	WiFi.begin(ssid, password);
 	while (WiFi.status() != WL_CONNECTED)
	{
    	delay(1000);
    	Serial.print(".");
  	}
  	Serial.println("\nConexión Wi-Fi establecida. Dirección IP: ");
  	Serial.println(WiFi.localIP());
}


void reconnect()
{
  	while (!client.connected())
	{
    	Serial.print("Conectando al broker MQTT...");
    	if (client.connect("ESP32Client", mqtt_user, mqtt_password))
		{
      		Serial.println("Conectado");
      		// Suscribirse al tema con QoS 1
      		client.subscribe(SUBSCRIBE_TOPIC, 1);
      		Serial.println("Suscrito al tema: ");
      		Serial.println(SUBSCRIBE_TOPIC);
    	}
		else
		{
      		Serial.print("Error: ");
      		Serial.print(client.state());
      		Serial.println(". Reintentando en 5 segundos...");
      		delay(5000);
    	}
  	}
}

/*
  this function only send a respone type of data.
  used for communication.
*/
void publishResponse()
{
  	StaticJsonDocument<256> doc_tx;

	doc_tx["id"] 	= ID;
	doc_tx["cmd"]  	= cmd;
	doc_tx["resp"]  = response;

	String json;
	serializeJson(doc_tx, json);
	Serial.println(json);

	publishMqtt((char*) json.c_str());

}


/*
  Parse the received json message and procces the recived commands
*/
void processCmd(byte* payload, unsigned int length)
{
	StaticJsonDocument<1024> doc_rx;
    //const char* json_rx = "{\"id\":\"anw00\",\"cmd\":\"gps\",\"arg\":1}";
    DeserializationError error_rx;
    //check for error
    error_rx = deserializeJson(doc_rx, payload,length);
    if (error_rx)
    {
		Serial.print(F("deserializeJson() failed: "));
		response = RESPONSE_ERROR_JSON;
		publishResponse();
      	Serial.println(error_rx.c_str());
    }
	Serial.println("prosesing Data");

    //parsing incoming msg
    rcvd_id = doc_rx["ID"];

    if( strcmp(rcvd_id,ID) == 0 )
    {
		JsonObject arg_js = doc_rx["arg"];

      	cmd = doc_rx["cmd"];

      	//prossesing incoming command
      	if(strcmp(cmd,"rst")==0)
      	{
        	response = RESPONSE_OK;
        	publishResponse();
			ESP.restart();
      	}
      	else if(strcmp(cmd,"v")==0)
      	{
			response = VERSION;
        	publishResponse();
      	}
		else if(strcmp(cmd,"mov")==0)
      	{
			channel  = arg_js["ch"];
			steps    = arg_js["ml"];
			moveStepper(steps, channel);
			response = RESPONSE_OK;
        	publishResponse();
      	}
      	else
      	{
        	Serial.println("Command not valid");
			response = RESPONSE_ERROR_CMD;
			publishResponse();
      	}
      	cmd = "";

    }
    else
    {
      Serial.println("msg not for me");
    }
}

// Función para mover el motor
void moveStepper(int _steps, int _ch)
{
	if(_ch < 0 or _ch > 3)return;

	ioport.digitalWrite(EN_PINS[_ch], LOW);
	digitalWrite(DIR_PINS[_ch], HIGH); // Configurar dirección (puedes ajustar según necesites)

	for (int i = 0; i < _steps; i++)
	{
    	digitalWrite(STEP_PINS[_ch], HIGH);
    	delayMicroseconds(500); // Ajusta según la velocidad deseada
    	digitalWrite(STEP_PINS[_ch], LOW);
    	delayMicroseconds(500); // Ajusta según la velocidad deseada
  	}

  	ioport.digitalWrite(EN_PINS[_ch], HIGH); // Deshabilitar el motor
}

void keyChanged()
{
	keyChange = true;
}


void measurePolling()
{
	for (uint32_t clock = 100000; clock <= 800000; clock += 100000)
	{
		Wire.setClock(clock);
		for (int i = 0; i < 1; i++)
		{
			//  reference time for keyPressed check UNO ~
			uint32_t start = micros();
			uint8_t index = keyPad.isPressed();
			uint32_t stop = micros();

      		Serial.print(clock);
      		Serial.print("\t");
      		Serial.print(index);
      		Serial.print("\t");
      		Serial.print(keys[index]);
      		Serial.print("\t");
      		Serial.println(stop - start);
      		delay(10);
		}
	}
}


//  -- END OF FILE --

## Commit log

2025-01-06 v2 of module version. fixing minor bugs and redistribute components on the board
    [export_cart_20241010_031501.csv, syringe_pump-B_Cu.gbl, syringe_pump-B_Mask.gbs, syringe_pump-B_Paste.gbp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]
2025-01-06 Deploying to docu-v2 from @ 389b25fcc70ce03c4f44ef68897344b781335110 🚀
2025-01-28 adding gerber files for V2
    [syringe_pump-B_Cu.gbl, syringe_pump-B_Mask.gbs, syringe_pump-B_Paste.gbp, syringe_pump-B_Silkscreen.gbo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]
